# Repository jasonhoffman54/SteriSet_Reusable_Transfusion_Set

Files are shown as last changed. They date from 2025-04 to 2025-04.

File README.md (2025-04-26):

# Reusable Blood Transfusion Set – Handoff Documentation

This repository contains all files related to the development and handoff of a reusable blood transfusion set for the Pothawira Surgical Center in Malawi. The goal of this project is to provide a cost-effective, sterilizable, and sustainable solution to address critical blood transfusion needs in low-resource settings.  
It is intended as a resource and starting point for future teams at the Malawi University of Business and Applied Sciences (MUBAS) and other collaborators working to continue and improve the project.

---

## Repository Structure

### `STEP_Files`
- **Description:** Contains CAD files for the transfusion set design, organized into STEP files for different versions of the set.
- **Subfolders:**
  - `STEP Files`: Includes design iterations.
    - `V1 Transfusion Set`: Initial design components.
    - `V2 Transfusion Set (Working)`: Updated working designs.
    - `V3 Transfusion Set`: Latest version with improved locking mechanism and flow regulation.

### `Design`
- **Description:** Documentation related to the design process.
- **Subfolders:**
  - `Brainstorming`: Contains initial ideas, parts research, and material notes.
  - `Trade Studies`: Includes comparative analysis of design options.

### `BME462_Documentation`
- **Description:** General documentation for the project when in the bme 462 course.
- **Subfolders:**
  - `Meeting+Interview_Notes`: Notes and audio files from interviews and meetings.
  - `Oral_Presentations`: PowerPoint files for team presentations.
  - `Writing_Assignments`: Comprehensive written reports on project progress.

### `Handoff_Documentation`
- **Description:** Core documents intended for project continuation and future development at MUBAS.
- **Contents:**
  - `Handoff Outline`: Overview of project status, unresolved challenges, and recommendations.
  - `Bill of Materials`: Detailed list of components and materials used.
  - `Outsourcing Documentation`: Information to support sourcing and manufacturing.

### `Regulatory_Standards`
- **Description:** Regulatory and compliance documentation for the transfusion set.
- **Subfolders:**
  - `Data_Sheets`: Specifications and material details, including the Infinity Bond adhesive datasheet.
  - `ISO_Documents`: Relevant ISO standards for compliance.
  - `Malawi Regulations`: Overview of Malawian regulatory requirements for medical devices.

### `Testing`
- **Description:** Testing protocols and results for evaluating the performance and reliability of the design.
- **Subfolders:**
  - `Testing_Protocols`: Procedures and metrics for verification and validation.
  - `Testing_Results`: Results and analysis from executed tests.

### `Presentation_Material`
- **Description:** All final presentation materials used during the project timeline.
- **Contents:**
  - Presentation posters, slides, and supporting visuals from design reviews and final presentations.

---

## Contributions
This project has been made possible by the efforts of:

- **Team Members:**
  - Jason Hoffman
  - Hannah Kragt
  - Darcy Ayers
  - Michaela Harris

- **Advisors and Contributors:**
  - Dr. Anne Alaniz, DO
  - Dr. Joanie Hope, MD
  - Dr. Nancy Kragt, DO
  - Dr. Megan Madonna, Ph.D.
  - Matt Brown
  - Kerry Eller
  - Duke Pratt School of Engineering

---

## Project Handoff Note
This repository is designed to support the continuation and future development of the reusable blood transfusion set project. We encourage future teams to build upon these materials, continue design refinement, pursue regulatory alignment, and adapt the device to meet the evolving needs of healthcare providers and patients in Malawi.

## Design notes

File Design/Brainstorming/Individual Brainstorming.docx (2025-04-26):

Individual Brainstorming

Darcy

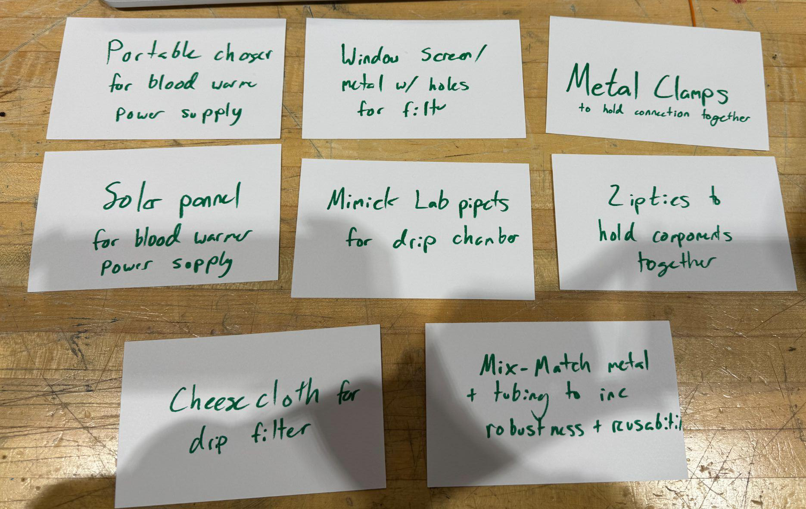
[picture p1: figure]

- Portable charger
  - Considers the power outages in Malawi
  - Meets the design criteria of using low-power
  - Meets the design criteria of being compact
  - Does not meet the design criteria of resource availability in Malawi
- Window screen/metal mesh
  - Meets the design criteria of sterilizable, reusability, and mechanical robustness
  - Depending on the material, this idea could fail in terms of resource availability and cost
- Metal connections
  - Meets the design criteria for sterilizable, reusability, mechanical robustness
  - This could not provide an air-tight seal, depending on whether there is no additional connections, such as glue
- Solar panel
  - Again, this accounts for power outages in Malawi
  - Meets design criteria for using low power and resource availability
  - Fails the design criteria of being compact
- Lab pipette for drip chamber
  - This material would allow for the flexibility we want in the chamber
  - This idea meets none of our major design criteria
- Zip ties for flow regulation
  - This allows for proper flow modulation
  - Meets the design criteria for sterilizable, reusability, cost, and ease of use
  - Fails the design criteria for resource availability and mechanical robustness
- Cheesecloth for filter
  - This would provide the design to filter out blood clots, however, the holes may be too large to efficiently filter.
  - Meets the design criteria for resource availability and cost
  - Fails the design criteria for sterilizable, reusability, and mechanical robustness
- Metal tubing in some locations
  - This idea was mainly to think of ways to make our tubing more robust
  - Meets the design criteria for sterilizable, reusability, mechanical robustness, and cost
  - Might fail the design criteria for air-tight seal due to additional connections

Hannah

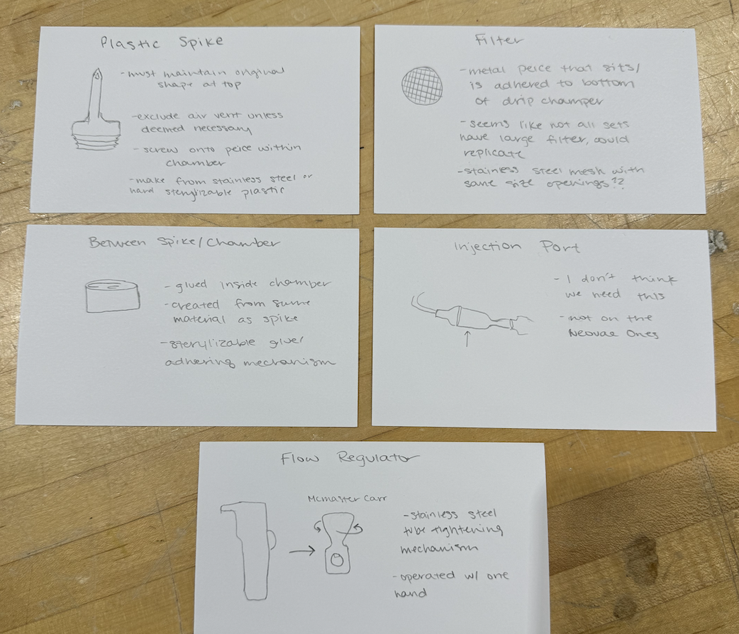
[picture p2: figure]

Jason

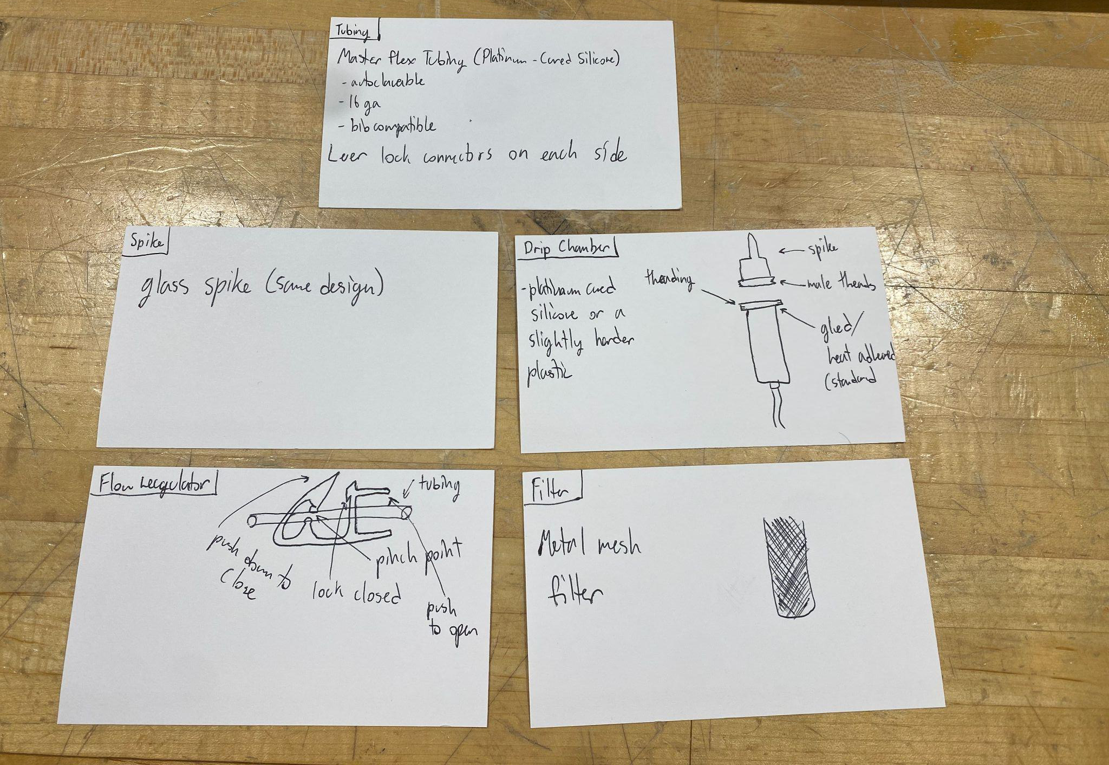
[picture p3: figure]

- Masterflex Tubing:
  - I found this steralizable tubing through research and it seemed perfect for our project
  - Meets design criteria of being autoclaveable, and biocompatible
  - The only part not considered is if the luer locks will hinder the sterilization process
- A Glass spike was thought to be a spike made of an easily sterilizable material.
  - Meets the design criteria of sterilizable and would be compatible with the blood bags
  - Does not consider the damage that could be done to the blood bag if too sharp
  - Does not consider durability and the likelihood that it will be broken in the clinic
- The Drip Chamber idea was thought to use the same material of the tubing that i found and make the spike attach to the drip chamber using a screw-on set with hard plastic or metal to make the chamber open and sterilizable.
  - Meets the design criteria of sterilizable and easy to assemble.
  - Does not consider what kind of adhesive we will use to attach the components
- The Flow regulator design was a design that I had seen online that i later found out was called a Robert Clip.
  - Meets the design criteria of being easy to use and sterilizable if made out of the right material.
  - Is not sufficient to provide a range of flow modulation in both increasing and decreasing flow
- The filter design was just a thought to make a metal mesh filter
  - This meets the design criteria of being a sterilizable material, however, does not consider whether the mesh size or porosity of the mesh will affect the sterility of the mesh
  - Would need to consider corrosion and other factors that would play into choosing the right metal
  - Also does not consider geometry for this filter which would have a large impact on the design.

Michaela

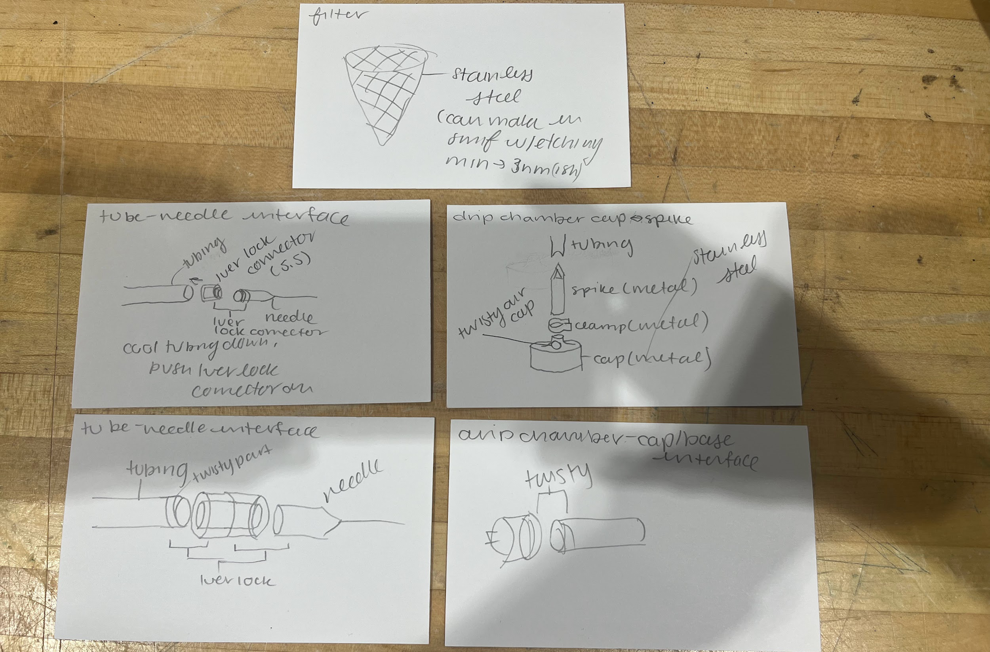
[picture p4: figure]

- Design 1 - Filter
  - Filter made out of metal mesh
  - Sterilizable, durable, reusable, easy to source
  - May be hard to assemble depending on how we put into drip chamber
  - Large surface area = faster blood filtration rate
- Design 2: Tube-needle interface
  - Tube- needle interface
  - Luer lock is airtight, easy to assemble, sterilizable, durable after many uses
  - Medical grade epoxy glue will ensure the strength of the connection from the tube to the luer lock
- Design 3: drip chamber cap/spike
  - Fit into each other
  - Lots of components makes it hard to assemble but improves sterilization capabilities
  - More components may mean less tight
  - Air vent not necessary if we have squishy bags
- Design 4: Tube-needle interface
  - Dual end luer lock connector with threads on tubing
  - Threads on tubing not feasible if have a bending material, would not be airtight and would be difficult to use
- Design 5: Drip chamber - cap/base interface
  - Have screw in for the cap and chamber
  - Airtight, easy to use, increases exposable surface area in autoclave
  - May have to use epoxies and additional components to finalize screw in

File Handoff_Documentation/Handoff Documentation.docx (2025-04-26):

# Project Overview

## Project Name & Description

Name: Reusable Blood-Giving Set for Pothiwira Surgical Center

The project focuses on developing an affordable, reusable, and sterilizable blood-giving set for the Pothawira Surgical Center in Salima, Malawi. Given the region’s high maternal mortality rate and limited access to blood transfusion supplies, the clinic faces critical shortages that delay life-saving procedures. The design integrates a durable twist-and-lock mechanism, a redesigned drip chamber for enhanced filtration, and a roller clamp for precise flow regulation. Materials such as platinum-cured silicone and stainless steel ensure biocompatibility and sterilization compliance. Testing confirmed the system’s ability to withstand compressive forces and effective bacterial removal after autoclaving. This solution aims to provide a sustainable alternative to single-use transfusion sets, improving patient care and healthcare accessibility in the region.

## Objective & Goals

Our primary goals for our project are:

1. Our design must be safe and sterilizable by passing tests that include bacterial removal, blood adhesion, and biocompatibility.
2. Make our design be durable, withstanding certain compressive strength and a drop test.
3. Ensure that our design is functional, including being easy to use, having no leakage, having flow modulation, having filtration, and is a compact size similar to standard disposable blood-giving sets.
4. Our design must fit community design requirements, including community comfort, use locally sourced materials, and low cost.

## Bill of Materials

Bill of Materials (https://docs.google.com/spreadsheets/d/1cqrfP7p347UXdv-eoOeXX8uZQHe5CB9nxKuMcwCITTk/edit?usp=sharing)

# Testing Procedures & Results

- Since we have all our testing from last semester already included in the git, maybe just add this new test to that document and link here?

# Assemebly & User Guides

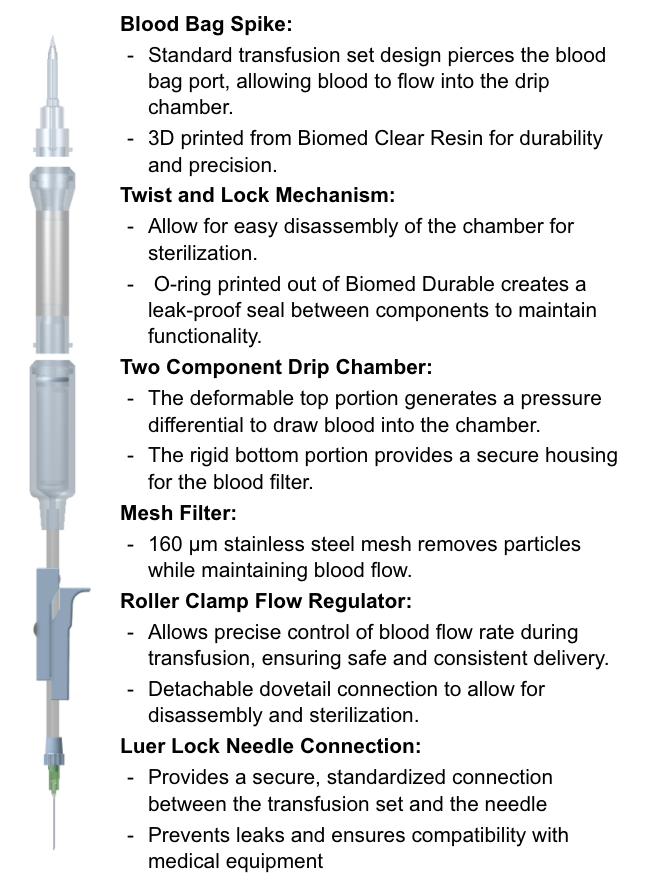
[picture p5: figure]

## Assembly of Set

1. Obtain the components listed above
2. Place the filter inside the rigid drip chamber
3. Twist and lock the flexible drip chamber to the rigid drip chamber
4. Attach the flow regulator to the tubing from the rigid drip chamber
5. Twist and lock the other side of the drip chamber of the spike
6. Attach the needle connection to the bottom of the tubing from the rigid drip chamber

## Disassembly & Sterilization of Set

1. Throw away the needle
2. Deconstruct the transfusion set by untwisting the spike from the flexible drip chamber and the rigid drip chamber.
3. Remove the filter cage from the rigid drip chamber
4. Place the 5 separate components (spike, flexible drip chamber, rigid drip chamber, and flow regulator) into the wash prior to autoclaving
5. Transfer the components into the autoclave and start a cycle of sterilization for 30 minutes at 121 ° C
6. After the cycle completion, remove the components

# Next Steps & Recommendations

### Unresolved Challenges

Adhesive Selection:
Finding a fully compliant adhesive remains an unresolved challenge. Both DOWSIL 734 and Infinity Bond adhesives failed to meet durability, biocompatibility, or sterilization requirements. Future work must identify a medical-grade, ISO 10993-certified adhesive capable of withstanding repeated autoclave cycles.

O-Ring Sizing and Performance:
The current O-ring design requires excessive compression at full engagement and does not provide a consistent seal across the locking range. Redesigning the O-ring geometry and groove depth is essential to create a reliable seal without placing unrealistic demands on assembly force.

Tolerancing of Components:
Variability in printed part dimensions has resulted in inconsistent assembly, poor sealing, and occasional mechanical failures. Further refinement of CAD models and manufacturing processes is necessary to achieve tighter dimensional control and consistent fit across all components.

Blood Adhesion and Surface Geometry:
Testing revealed residual blood in complex geometries and in sections with adhesive, posing a risk for incomplete sterilization. Smoother surface transitions, larger radii, and minimized internal crevices in addition to a medical grade adhesive are needed to improve sterilization outcomes and minimize infection risks.

### Design Change Recommendations

### Source a Medical-Grade Adhesive: The team should prioritize identifying a biocompatible, autoclavable adhesive, such as a medical-grade two-part silicone or epoxy. Early validation testing is critical to ensure that the new adhesive maintains strength and integrity through sterilization cycles.

Revise O-Ring Design:
Future prototypes should incorporate thicker O-rings and deeper seating grooves to allow gradual compression and better sealing. Expanding the compression zone can help accommodate small tolerancing inconsistencies without sacrificing seal integrity.

Introduce Modular Tubing Replacement:

Consider a design where the tubing is detachable and disposable after each use, while the hard components remain reusable. Quick-connect fittings could make the device safer, easier to sterilize, and better aligned with clinical workflows.

Improve Surface Geometry:
Components should be redesigned with polished surfaces, rounded internal geometries, and minimized seams to reduce blood adhesion. Post-processing of 3D-printed parts could further enhance sterilization efficacy.

Expand Mechanical and Functional Testing:
Subsequent prototypes should undergo full mechanical validation, including tensile, fatigue, and high-pressure leakage testing. Aligning testing protocols with ISO 1135-4:2015 standards will help prepare the device for future clinical approval and deployment.

## Key Partners and Contacts for Follow-up

Student Team Contacts

Hannah Kragt - hannah.kragt11@gmail.com

Jason Hoffman - hoffman.jason21@gmail.com

Darcy Ayers - darcy.ayers@gmail.com

Michaela Harris - mharris3002@gmail.com

Advisor Contacts

Megan Madonna - megan.madonna@duke.edu

Partner Contact

Anne Alaniz - abalaniz@houstonmethodist.org

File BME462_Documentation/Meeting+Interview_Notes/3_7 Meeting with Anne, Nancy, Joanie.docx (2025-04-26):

Meeting Outline

- Let them know we didn’t get Rice360
- Update on where we are with the project
  - Show them new printed parts (twist and lock, two part modulator, etc.)
  - Complications
    - Resin choice
      - Moving to either biomed durable or clear
    - Adhesive:
      - Darc update
        - Meets biocompatibility standards
        - Compatible with most sterilization techniques (good for 1st q)
      - Do they know of permanent, sterilizable adhesives?
    - Orings
      - Need platinum cured medical grade
      - Only ones we found quotes 60+ per
  - Future plans
    - Micheala testing
    - Handoff documentation
    - IP to hand off to MUBAS
      - Plan to hand off in spring
- Questions
  - If this is meant to one day be used at more than just Pothawira, should we be aiming to have a product that can be sterilized by a different technique
    - Have pots that they boil?
    - Chemical sterilization (spirit)
    - Most hospitals have autoclave
    - Will you have any other techniques at Pothawira Surgical? (Ex. Ethylene oxide ETO, Gamma irradiation, chemical disinfection)
  - Have any of you guys had experience with the regulation and approval of medical devices in Malawi / medical regulations in general with Pothawira?
    - Aida (public health) (Maggies sister) - connect that knows more about regulation and process
    - Ask Andrew (MUBAS)
- Questions from Anne, Nancy, and Joanie
  - Test to see if all sterilization techs are =, and device maintains structure
  - Is there a # of uses for the sets?

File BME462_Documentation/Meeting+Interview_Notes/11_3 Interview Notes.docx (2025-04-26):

Preplanning

- Go over the current solution
  - Ask about the need for an air vent
  - Ask about what type of needles they have or see if they could send us what brand of needles they have
  - Show the filter cage and say how there is a metal mesh
- How do we plan to change the current solution
  - Increase the diameter of the chamber
  - Twist and lock with silicone bumper for air tightness
- Go over the testing plan
  - Ask for advice on doing the community comfortability survey

Meeting Notes with Joanie and Anne 11/3/2024

Design

- shared design with stl files
- asked material - biomed resin, biocompatible, autoclavable
- confused about filter part - explained
- We dont have air vent - do you guys use it
  - Guess - get rid of air bubbles
  - ask lab guy they will be working with in salima what the air vent is for
  - asked nurse - too modern based on how they do it \
  - Maggie and matthew would know better - so will lab guys
    - she will send message to him
  - Put pictures of what we have right now in the group, she will send message to lab guys
- Talked about threaded components and issues we are worried about in the future pertaining to thread wear over time
  - liked the idea of making a slot connection and wanted to see what that would look like
  - Plan to do that in next prototype
- they asked if we have a way to modulate the flow
  - we have flow regulator, ok with design being the same
- asked about connection to needle, what does it look like there?
  - needles available
  - asked for pictures from them
- they asked if theres any part of system thats disposable
  - needle
- they asked how long is the tubing
  - 3-4 feet
  - based on standard sizing

Testing

- explained testing plan
- going to forward the testing metrics to them
- could ask them, translate, load them onto google doc
- on the ground they can print out survey, have patients answer questions when tyey come through the clinic
  - have a high volume clinic
- transfer, fill in on paper, put it back into google form for answering
- surveys
  - community members
    - comfort, don’t want to intimidate them
  - nurses
    - ease of use
  - one prior to any sort of use - ease of use, how does it feel, what does it look like
  - actual use = be different and more rigorous
  - Feedback from nurses for actual use
  - Patients be minimally frightened by the device
  - nurse - before using it and after using it survey
- Just got wifi and computers to facility - fast for staff (also english speaking) → make survey taking easier

Notes to update things from them

- Have 2 surveys for nurse
  - before use (autoclaving, ease of use)
  - using for patients
- is blood tested before it touches our set → yes
  - get packed RBCs
  - giving blood, do basic testing
    - HIV, HEPB, HEPC, hemoglobin

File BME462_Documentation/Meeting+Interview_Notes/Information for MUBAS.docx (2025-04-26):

Reusable Blood Transfusion Sets

Collaboration with Pothawira

Pothawira (Safe Haven) Christian Mission Organisation, based in Salima, Malawi, serves the community by providing housing, healthcare, education, and economic sustainability projects. The campus includes a medical clinic, birthing center, primary school, and a home for 124 orphaned children. Recently, funds were raised, and plans were made to open a new surgical center in 2025. This is crucial as the only other surgical center in the region, Salima District Hospital, has just two OR rooms, neither adequately equipped for optimal surgical procedures and insufficient to serve the needs of 800,000 people.

Blood Donation

Pothawira’s new surgical center will be equipped with a blood bank. Blood donation is a critical issue in Malawi, as the Salima District Hospital blood bank frequently lacks sufficient supply. Patients are required to bring a family member with the same blood type to be on standby for potential transfusions. This challenge is exacerbated when blood-giving sets are unavailable, as the Malawi Government provides a limited supply of these sets to the local hospital, but more are needed to reach the demand. This unfortunately leads to situations where necessary blood cannot be provided during surgery.

Needs Statement

The current method for blood transfusions at the Pothawira Surgical Center in Salima, Malawi, relies on on-site blood gathering, testing, and donation from a patient’s family member with the same blood type. The clinic lacks the ability to store blood donations and frequently runs out of necessary equipment for blood transfusions, leading to critical delays in patient care. The local population, which includes over 800,000 residents, is in urgent need of reliable and efficient transfusion methods. There is a need for affordable, reusable, and sterilizable blood-giving sets and a blood-warming device that can safely warm stored blood to the optimal transfusion temperature. These devices must be durable, compatible with existing equipment, and made from locally available materials to ensure sustainability, improving patient outcomes, and meeting the operational demands of the new blood bank and surgical center opening in 2025.

# Part 3:

Design criteria

1. Sterilizable (Must Have)

Justification: The blood-giving sets must be made with components that can withstand sterilization procedures used at the clinic (e.g., high-temperature cleaning). The blood-warming device must also be sterilizable to maintain safety in blood handling and administration.

Verification: We will test the device's components by subjecting them to multiple cycles of sterilization (e.g., autoclaving at 121°C for 30 minutes) and evaluating their structural integrity, material degradation, and cleanliness. Each component will undergo at least 50 sterilization cycles to verify long-term usability without degradation (21).

2. Locally available resources

Justification: The device should be made from materials that are available or easily accessible in Malawi to ensure long-term sustainability and reproducibility. This will reduce dependency on external suppliers and allow local healthcare providers to maintain and replicate the device.

Verification: A conversation will be conducted with local suppliers and healthcare providers in Malawi to confirm the availability of materials needed to manufacture the devices.

3. Cost under $100 for blood-giving sets

Justification: The cost of the devices must meet the budgetary constraints of the clinic and the Malawian healthcare system. These numbers are safe upper limits for cost, given by our sponsor. The affordability will ensure that the devices can be widely used and sustained in the resource-limited setting.

Verification: A cost analysis will be conducted by sourcing material quotes from local and international suppliers, along with labor costs. We will ensure the final production cost remains within the specified range.

4. Air-tight seal Justification: The blood-giving sets must maintain an air-tight seal to prevent contamination and ensure the safe transfer of blood. This is essential to avoid infection risks and maintain the integrity of blood during transfusion.

Verification: We will test the air-tightness by applying water or air pressure to the system and ensuring no leaks occur under typical use conditions. The system will also be tested under vacuum conditions to simulate blood flow during transfusion.

5. Reusable, Durability to withstand 200 uses Justification: The blood-giving sets must be reusable and durable enough to withstand multiple sterilization cycles and uses without degrading. This will ensure that the investment in each set maximizes its long-term use and reduces the need for frequent replacements.

Verification: The devices will undergo mechanical fatigue testing by simulating repeated use, including sterilization cycles, disassembly, and reassembly.

6. Portability and easy-to-use design Justification: The device should be portable and easy to use by healthcare workers with minimal training. This will facilitate use in various settings within the clinic and ensure the device can be employed efficiently during emergency situations.

Verification: The device’s portability will be verified by ensuring it weighs less than 2 kg and can be easily transported by a single healthcare worker between rooms. Ease of use will be validated through usability tests where healthcare workers will be able to set up the device within 10 minutes and operate it effectively after no more than 30 minutes of training.

7. Mechanical robustness and resistance to mechanical stress Justification: The devices must be able to withstand rough handling, transport, and drops in a busy clinic environment without breaking or malfunctioning. According to WHO standards, medical devices in resource-limited settings must be rugged and able to withstand rough handling, transport, and frequent use. This ensures longevity and reduces the cost of repairs or replacements.

Verification: The devices will be subjected to mechanical stress tests, including drop tests from 1 meter and impact resistance tests. Components will also be tested for fatigue by applying repeated pressure and strain.

8. Compact design for storage

Justification: The blood storage device must be of comparable shape and size to existing blood bags to fit seamlessly into the current blood storage infrastructure at the clinic. This ensures compatibility with existing refrigeration and storage systems, reducing the need for modifications or additional storage solutions.

Verification: We will compare the dimensions of the blood storage device to standard blood bags (approximately 10-15 cm in width and 20-25 cm in length) and test its fit in clinical storage units. The device must occupy the same space as a typical blood bag in refrigerators and storage racks used at the clinic, ensuring it integrates smoothly with the current setup.

9. Community Comfortability

Justification: The blood-giving set must be as non-intimidating as the current disposable sets to ensure patient comfort and acceptance, supporting a smooth transition and consistent use.

Verification: Surveys will compare patient comfort levels using a Likert scale, assessing the new set against existing disposable sets. Usability tests will gauge willingness and preference through direct comparison feedback.

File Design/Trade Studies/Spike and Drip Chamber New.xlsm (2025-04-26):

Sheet: Start Here
Trade Study Template for MS Excel
Version 2.0
Copyright © 2014 by Jeffrey Ellis. All rights reserved.
http://jeffreyellis.org
*** START HERE *** The Trade Study Template for MS Excel is a spreadsheet that implements a simple weighted sum method for multiple criteria decision making. It is a .xlsm file that should work with Excel 2007 and later. Instructions: 1. Read the license agreement on the License worksheet. Your continued use of this template constitutes agreement with this license. 2. In the Raw Data worksheet, enter your alternatives under consideration and your evaluation criteria, and enter the raw scores for evaluation criteria for each alternative. 3. In the Utility Functions worksheet, enter the data required to define the utility functions that transform raw scores into utility (on a scale of 0.0 to 1.0) for each evaluation criteria. 4. In the Evaluation worksheet, set and adjust the weighting factors for your evaluation criteria. This worksheet also displays a stacked bar chart of the results, with the alternatives sorted in ranked order. 5. In the Sensitivity Analysis worksheet, you can perform sensitivity analysis on any selected criteria.
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

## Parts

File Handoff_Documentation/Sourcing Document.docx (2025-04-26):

Platinum Cured Silicone O-rings

Fluid Path Products (https://www.fluidpathproducts.com/_files/ugd/faea02_0909baf2fb4c4fbfb870d9c755825b22.pdf)

- Have clear, platinum cured silicone O-rings in stock
- Need to know size, and quantity
  - If size the have already in stock, could receive relatively quickly
- Email: carlyb@fluidpathproducts.com
- ISO 10993 Compliant

Biocompatible Permanent Adhesive

- Needs to meet ISO 13485 an ISO 10993

Elastosil E43 N

- What we tried to originally purchase last semester
- Having a hard time finding a good sourcing location
- SkyGeek (https://skygeek.com/wacker-chemie-elastosil-e43-rtv-1-silicone-rubber-adhesive-90-ml-tube.html?gad_source=1&gbraid=0AAAAAD_KchHeS3hvwVfQXH2fucgE1NsRO)

Vitralit 4731 (https://www.panacol.com/panacol/datasheets/vitralit/vitralit-4731-english-tds-panacol-adhesive.pdf) & Vitralit 7041 F (https://www.panacol.com/panacol/datasheets/vitralit/vitralit-7041f-english-tds-panacol-adhesive.pdf)

- Need to be cured by UV/Visible Light
  - Confused if this means we need LED or not

Master Bond (https://www.masterbond.com/products/silicones-medical-devices)

- Mastersil 151 Med

GlueGun (https://www.infinitybond.com/products/infinity-bond-medical-device-cyanoacrylate-super-glue?variant=31582833901702)

# Infinity Bond Medical Device Super Glue Cyanoacrylate

  - 220 $
  - Requested TDS and SDS to confirm if usable
- Got TDS and SDS, emailed to try and get a sampe - if no response today will call tomorrow

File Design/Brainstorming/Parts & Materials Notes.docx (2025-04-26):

Blood Giving Sets

PVC: Gamma and sterilization stability, Migration resistance, Color consistency, Thermal stability, RF and solvent welding, Printability (link (https://www.eastman.com/Markets/Medical-Supplies/Pages/Medical-Tubing-Bags.aspx))

1. Bag
  a. Saline: Polypropylene (PP) - Sterilized by water cascade terminal sterilizer in house; eliminating the need for 3rd party sterilization services (link (https://isikel.com/manufacturing/saline-bags/))
  b. PVC
    i. 42 day shelf life
  c. Needs to have a port for donation and a port for transfusion (most had 3 ports tho?)
  d. If reusable must be resealable after donation/transfusion
  e. Needs anticoagulants (and for them to be replenished with each use
2. Protector
  a. Polyethylene (PE) - sterilizable
3. Plastic Spike
  a. Acrylonitrile butadiene styrene (ABS) - ABS can be sterilized, but not with an autoclave or gamma sterilization
4. Air Vent
  a. Stainless steel, ABS, or POM (polyacetal). The spike is encased in polyamide
  b. Air vent (https://www.kmedhealth.com/difference-between-vented-and-non-vented-iv-sets/) isn’t absolutely necessary unless transferring from rigid container
5. Drip Chamber
  a. DEHP PVC or Non-DEHP PVC - potentially toxic?
  b. Polyethylene terephthalate (PET or PETE) - sterilizable and flexible
  c. Drip Chamber + Spike (https://www.kmedhealth.com/product/drip-chamber-with-spike-48mm-and-50mm/)
  d. Needs to be able to be compressed
6. Filter
  a. Polypropylene (PP)
  b. Basic mesh filter with pore size of 170-260 microns
  c. https://sharevfilters.en.made-in-china.com/product/KmNrbVyYgnRP/China-Blood-Filter-for-Transfusion-Set.html
  d. Metal mesh with 125-micron filter link (https://www.amazon.com/Stainless-Steel-Filter-Screen-Filtration/dp/B07QNTQ13L?hvadid=693071814667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)
  e. Watchman device for LAA - PET fabric material link (https://www.watchman.com/en-us-hcp/about-the-procedure.html)
7. Tubing
  a. PVC and sometimes DEHP to add flexibility
8. Flow regulator
  a. PE or ABS
  b. Potentially could make from metal/order metal component
    i. https://www.mcmaster.com/5330K16/
    ii. https://www.mcmaster.com/products/pinch-valves/
9. Injection site
  a. Latex or Latex free
  b. Rubber Bulb Injection Site (https://www.kmedhealth.com/product/rubber-bulb/)
10. Luer Lock Connector
  a. ABS
  b. Pre-made order?
  c. Will need connectors for each component not necessarily this type but airtight and reusable
11. Needle
  a. Non sterilizable/ reusable
12. Other material links
  a. https://www.kmedhealth.com/types-of-iv-set-injection-sites/

Wednesday

- Understanding of how each component works

First prototype

1. Blood bag - Ziploc bag
2. Plastic spike -
3. Drip chamber - squeeze bottles
4. Filter - cheese cloth
5. Tubing - tubing or plastic straws
6. Injection site
7. Luer lock - plastic syringe luer lock
8. Needle - sewing needle

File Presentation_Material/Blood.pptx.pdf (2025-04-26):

# Reusable Blood Giving Sets for Pothawira Surgical Center

## Hannah Kragt, Jason Hoffman, Micheala Harris, and Darcy Ayers - Fall 2024

## Design Project Goal

Our project aims to create an affordable, reusable, and sterilizable method for blood-giving sets to address the limited availability of single-use sets for the Pothawira Surgical Center in Salima, Malawi.

## Background and Motivation

- High Maternal Mortality Rates:
– 25th highest maternal mortality rate in the world¹
– Blood loss due to postpartum hemorrhaging (PPH) is the leading cause of maternal mortality³
- Challenges in Blood Supply:
– Salima, Malawi, serves a population of 560,000 but only receives 10 units of blood per week from the government⁴ – Blood has a very short shelf life, often lasting less than 4 hours without proper storage⁵
– Blood is only donated when a relative is in urgent need⁴
- Inadequate Healthcare Facilities:
– Patients commute 2 hours away to get transfusion sets⁴ – Many women give birth on the floor of clinics without adequate care or clean environments⁴
- Current solutions are not sustainable
– Disposable solutions are not easy to source or store⁴

## Final Design Solution

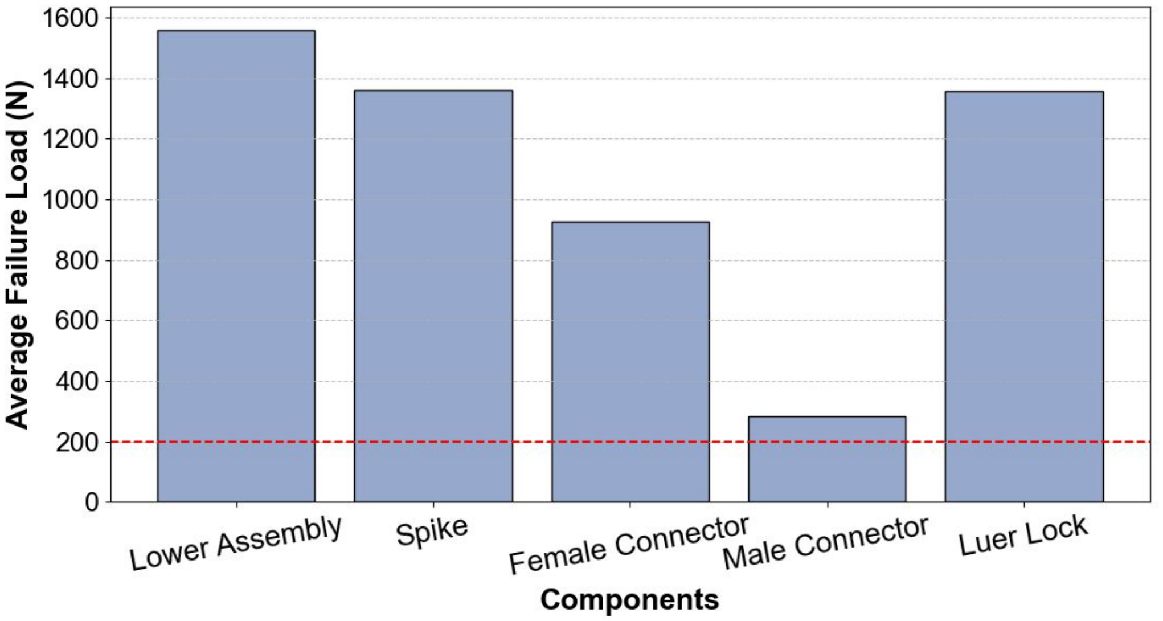
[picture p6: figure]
Temperature: 37.0°C

We would like to extend our thanks to the following:
- Dr. Anne Alaniz DO
- Dr. Joanie Hope MD
- Dr. Megan Madonna Ph.D.
- Matt Brown
- Kerry Eller
- Duke Pratt School of Engineering

## Acknowledgements

## Results

## Conclusions and Future Work

- Twist-and-Lock Mechanism: Replaced screw-in components with a twist-and-lock system for durability, airtight sealing, and ease of use, using a platinum-cured O-ring
- Redesigned Drip Chamber: Larger chamber for robust, industry-standard filtration
- Enhanced Flow Modulator: Improved modulation control, ridged roller, stronger walls, removable design
- Sealant Replacement: Identify a biocompatible alternative to DOWSIL 734 to ensure compliance with ISO 10993 standards

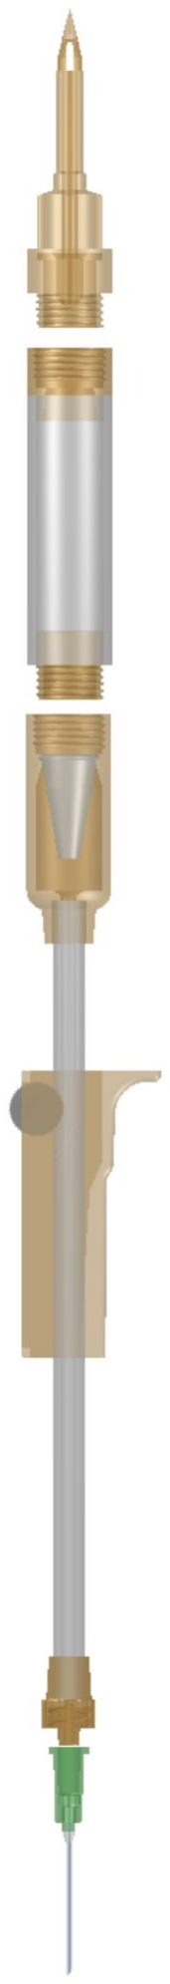
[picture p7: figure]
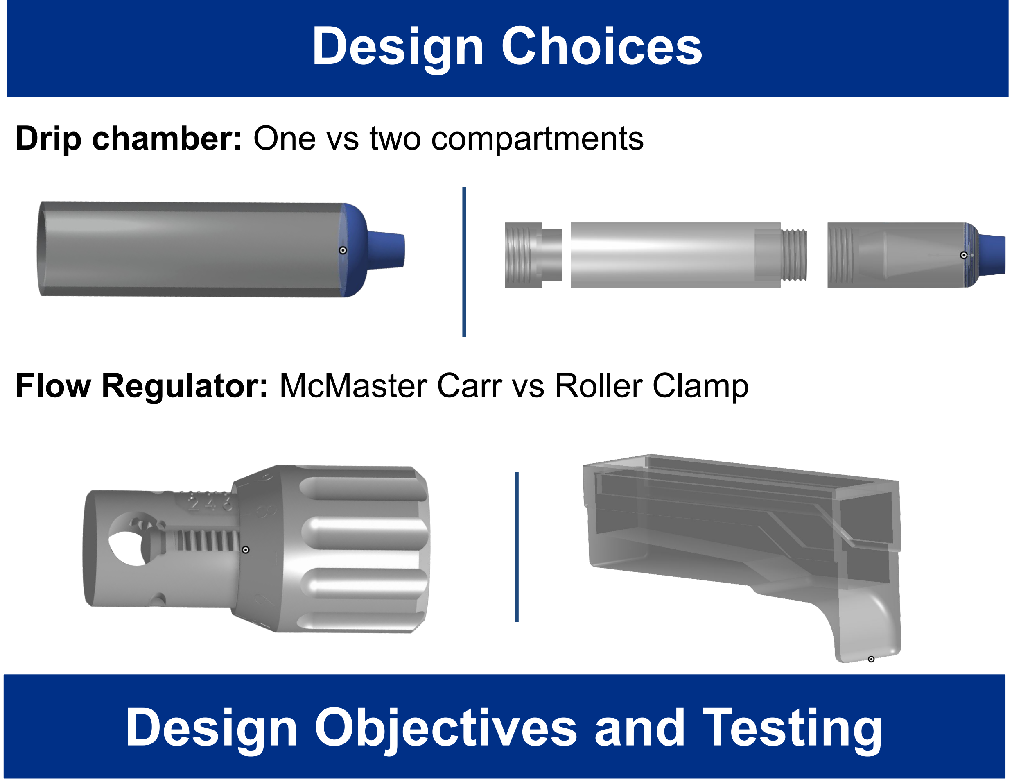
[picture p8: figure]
Design Objectives and Testing; Design Choices; Drip chamber: One vs two compartments

Design Objective | Test | Results
Ensure effective bacterial removal from the set after sterilization | Autoclaved components (clamp, mesh, tubing) at 121°C for 40 min; 10 analyzed bacterial growth (E. coli) using ImageJ | PASS - No bacterial growth observed
Transfusion set is leak-proof during use | Assembled set with Ziploc bags filled with water; simulated use and observed for leakage at connections | PASS - No significant leakage in 5 tests; minor leakage in 1 test due to puncture seal
Verify that all materials in the set are biocompatible and met ISO 10993 standards | Reviewed material data sheets and product descriptions for compliance with biocompatibility standards¹¹ | FAIL - Majority of materials passed; Dowsil 734 Sealant failed, requiring replacement
Components can withstand a minimum lateral compressive load of 200 N | Applied lateral force using a vice and measured load at failure with a high-capacity scale | PASS - All components passed
Cost-efficient for affordability in resource-limited settings | Conducted cost analysis using BOM; calculated per-set cost based on material quotes | PASS - Total cost was $23.71 per set

Resin
(Roller
clamp)

Metal Mesh
(Filter)

Platinum-Cured
Silicone Tube

(-) Control
(glass
beaker)

(+) Control
(colonies in
tube)
Material | Use | Attributes
Biomed Amber Resin | 3D Printed Components | Biocompatible, rigid, 6 semi-transparent
Platinum-Cured Silicone | Tubing | Flexible, biocompatible, 7 sterilizable
304 Stainless-Steel Mesh | Filter | Corrosion-resistant, durable, 8 efficient
DOWSIL Flowable Sealant | Permanent Adhesive | Airtight, easy application, 9 food grade

## References

[1] CIA., “Maternal mortality ratio”, 2024
[2] Kalulu et al., “Determinants of teenage pregnancy in Malawi” BMC Women’s Health, 2024
[3] Beltman et al., “Beyond maternal mortality” Acta Obstet Gynecol Scand, 2011
[4] A. Alaniz and J. Mayer Hope, “The Blood Transfusion Set Deficiency In Salima, Malawi,” 2024.
[5] Brunskill et al., “What Is the Maximum Time That RBCs Can Be Left Out?,” Transfusion Med. Reviews, 2012
[6] Formlabs et al., BioMed Amber Resin Tech. Data Sheet, 2023.
[7] Avantor Fluid Handling et al., Cert. Qual. Tubing MFLEX Silicone No. 16, 2024.
[8] Xu et al., J. Mater. Res. Technol., 2024.
[9] Dow Chemical Company et al., DOWSIL 734 Flowable Sealant Tech. Data Sheet, 2020.
[10] CDC et al., Steam Sterilization 2024
[11] FDA et al., Use of ISO 10993-1 Guidance, 2023.
E. coli Removal Results: Device is able to be sterilized without bacterial growth after autoclaving

Blood Bag Spike:
- Standard transfusion set design pierces the blood bag port, allowing blood to flow into the drip chamber.
- 3D printed from Biomed Amber Resin for durability and precision.
Threaded Connections:
- Allow for easy disassembly of the chamber for sterilization.
- Create a leak-proof seal between components to maintain functionality.
Two Component Drip Chamber:
- The deformable top portion generates a pressure differential to draw blood into the chamber.
- The rigid bottom portion provides a secure housing for the blood filter.
Mesh Filter:
- 160 µm stainless steel mesh removes particles while maintaining blood flow.
- Designed with a lip for secure placement in the drip chamber.
Roller Clamp Flow Regulator:
- Allows precise control of blood flow rate during transfusion, ensuring safe and consistent delivery. Luer Lock Needle Connection:
- Provides a secure, standardized connection between the transfusion set and the needle
- Prevents leaks and ensures compatibility with medical equipment

Flow Regulator: McMaster Carr vs Roller Clamp

Compressive Failure Test Results: All components of device can withstand compressive force of 200N

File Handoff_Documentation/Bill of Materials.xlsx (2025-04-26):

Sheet: Sheet1
Material/Component | Link | Cost per unit | Data s

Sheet: Sheet2
Material/Component | Destributer | Link | Cost per unit | Data Sheet (if available) | Comments
Masterflex® L/S® Precision Pump Tubing, Platinum-Cured Silicone, L/S 16; 25 ft | MasterFlex | https://www.avantorsciences.com/us/en/product/NA5144597/masterflex-l-s-precision-pump-tubing-platinum-cured-silicone-avantor | $110 / 25 ft | 39649788.pdf (https://drive.google.com/file/d/1tNDcIT6IlDR5QIraNRWExZWtzMHCHnJR/view?usp=sharing) | Platinum-Coated Silicone Tubing (I.D: 3mm)
Cold & Colder Ultra Clear Pure Silicone Tubing by the foot | Cold & Colder | https://coldandcolder.com/collections/featured-products/products/silicone?variant=41786948157613 | $1.95 / ft | Cold & Colder Tubing (https://docs.google.com/document/d/1e-jHgzZKUy4-TXI4_C50p3UIj-2hbJyQbGJ7OiWKfCQ/edit?usp=sharing) | Platinum-Coated Silicone Tubing (I.D: 25.4mm)
Dowsil 734 Flowable Sealant | Dowsil | https://www.aerospheres.com/products/sealants/elastosil-e43-90-ml-tube/ | $52.40 | 95-1058-01-dowsil-734-flowable-sealant.pdf (https://drive.google.com/file/d/1FSC-Weza_c-cbWSuwQx6nmtAhDPpoqPI/view?usp=sharing) | Original Adhesive, Doesn't meet ISO 10993 Standard
Biomed Clear Resin | Formlabs | https://formlabs.com/store/materials/biomed-clear-resin/?_bt=715361922394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 | $349/L | 2001432-TDS-ENUS-0.pdf (https://drive.google.com/file/d/1d4uA7wYFVtt3jQ1FuF137jnkkdj8VKLk/view?usp=sharing) | For printing all rigid components, use roughly 60ml per print
Biomed Elastic Resin | Formlabs | https://formlabs.com/store/materials/biomed-elastic-50a-resin/ | $349/L | 2302832-TDS-ENUS-0.pdf (https://drive.google.com/file/d/1flWeDUGft7DmXhl38e5WYCV_0fZufky9/view?usp=sharing) | For printing compressable O-rings
304 Stainless Steel Woven Wire 80 Mesh 0.18mm Hole | Amazon | https://www.amazon.com/304-Stainless-Steel-Woven-Wire/dp/B07ZQ1ZCKJ?hvcampaign=business&gbraid=0AAAAA-bxZAHeOU6dPf0GyaMTzGCgFVEsY | $3.72/sq ft | Steel Mesh (https://docs.google.com/document/d/1AruYmwrgTkx_dW1E24qpgE6N79BoQdFs-MYufgR2YGg/edit?usp=sharing) | For the mesh filter

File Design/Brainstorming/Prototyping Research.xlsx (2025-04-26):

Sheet: Sheet1
Description | Material Purchase Links | CPU ($)
Sterilizable Tubing | link (https://us.vwr.com/store/item/NA5144597/masterflex-l-s-precision-pump-tubing-platinum-cured-silicone-avantor) | 20
Blood Transfusion Set Components | link (https://www.kmedhealth.com/what-is-a-blood-transfusion-set/)
Medical Grade Plastics | link (https://www.kmedhealth.com/what-are-medical-grade-plastics/)
Bulk Order links - luer lock, rubber bulb, rubber pad | link (https://www.kmedhealth.com/types-of-iv-set-injection-sites/)
Sterilizable drip chamber with method of creation and parts list | Transfusion Drip Chambers | GVS (https://www.gvs.com/en/catalog/transfusion-drip-chambers)
Pinch Clamps/Screw Clamps to replace flow regulator | link, link (https://www.mcmaster.com/5330K16/)
Elastosil E43 (90ML Tube)
Filter - holes in metal | Etched Plates for Filtering and Anti-dust (https://www.perforated-sheet.com/perforatedsheetapplication/etched-palates.html) |  | Could potentially make this in SMIF
Tubing - silicone, cheap, larger diameter than desired | https://www.govets.com/usa-sealing-inc-310-28569309.html

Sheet: Sheet2
MATERIAL | use | PRO | CON |  | blood bag
Glass | - Spike - Cap/base of drip chamber | Autoclavable | Breaks easily |  | spike
Rubber | - Blood bag - Rubber bulb | Autoclavable |  |  | tubing
Silcone | - Tubing - Drip chamber | Autoclavable (250ºC), cheap |  | https://www.govets.com/usa-sealing-inc-310-28569309.html | cap of drip chamber
Stainless steel | - Clamp - Filter | Autoclavable |  | https://www.perforated-sheet.com/perforatedsheetapplication/etched-palates.html | clamp
 |  |  |  |  | filter
 |  |  |  |  | drip chamber
 |  |  |  |  | base of drip chamber
 |  |  |  |  | rubber bulb
 |  |  |  |  | hypodermic needle

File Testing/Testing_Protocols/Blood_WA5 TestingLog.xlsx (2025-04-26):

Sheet: Master Plan
Design Requirements |  | Method of Verification (BOM, X type of testing, self-evident by dimension X, etc). | If you know there would be a method to test that you want to do, but in discussing with the instructional team know it may not be feasible within the class framework, make a secondary plan for a simulated testing procedure that may work towards the goal within the limits of the class in addition to the "If we could, we would do this" plan. |  | Reporting | Target Completion Date | Required Materials/Prep | Comments
 |  |  | Ideal Testing Plan (Lay out plan for testing generally, as detailed as possible) | Preliminary Testing Plan (Lay out plan for testing generally, as detailed as possible)
1.1 | Safety/Sterilizability
 | Bacterial Removal | Sterilization Testing | Add 1 mL of bacteria to each component and metal surgical tube. Incubate for 48 hours. Then wipe down with kimwipe for 15 seconds. Place component in autoclave. Once done, remove from autoclave, look under microscope for bacteria. | Add 1 mL of bacteria to each component and metal surgical tube, then wipe down with kimwipe for 15 seconds. Place component in autoclave. Once done, remove from autoclave, look under microscope for bacteria. | Determine and record % of surface area covered by bacteria at 5 different locations for both surgical-grade metal and each component | 2024-11-08 | Equipment and instruments needed: Autoclave, Each component of our device, Surgical-grade metal, Light microscope, Bacteria stock of Escherichia coli Reusable glassware/plasticware needed: Eppendorf tubes (1.5mL) x12 Disposable materials needed: Pipettes (1000µL), Kimwipes
 | Blood Adhesion | Performance Testing | Fill beaker with 10 ml of animal blood. Place medical-grade metal in beaker, place component in beaker, mix by swirling around with hand for 1 minute to simulate blood running along surface of material. Then extract component and medical-grade metal and place component and medical-grade metal in autoclave. Remove from autoclave and take photo of component and medical-grade metal for later reference. | Mix 5 mL PBS and 5 mL of red food dye in large 2000mL beaker. Place medical-grade metal in beaker, place component in beaker, mix by swirling around with hand for 1 minute to simulate blood running along surface of material. Then extract component and medical-grade metal and place component and medical-grade metal in autoclave. Remove from autoclave and take photo of component and medical-grade metal for later reference. | Remove from autoclave and take photo of component and medical-grade metal for later reference. Observe if any red dye is visible, qualitatively compare to amount visible on metal | 2024-11-08 | Equipment and instruments needed Red food dye, Phosphate Buffered Saline (PBS), Motorized pipette filler, Transfusion set components Reusable glassware/plasticware needed Beaker Disposable materials needed Serological pipette,Vacuum pipette
 | Biocompatibility | Self-evident by BOM | Compile a comprehensive Bill of Materials (BOM) for the blood-giving sets. Review data sheets for each material used in the design to verify biocompatibility. Cross-check materials against biocompatibility standards. | Compile a comprehensive Bill of Materials (BOM) for the blood-giving sets. Review data sheets for each material used in the design to verify biocompatibility. Cross-check materials against biocompatibility standards. | Compile biocompatibility of all materials and summarize findings in testing document | 2024-11-08 | List of materials and corresponding BOM for each material
2.1 | Durability
 | Compressive Strength | Strength Testing | Prepare each component of the blood-giving set for testing by measuring its initial dimensions using calipers. Place the component into the compression testing machine. Apply a gradually increasing compressive force until the component breaks or malfunctions. Record the maximum load at failure for each component. Repeat the test for each individual component of the blood-giving set 3 times each. | Prepare each component of the blood-giving set for testing by measuring its initial dimensions using calipers. Place the component into the compression testing machine. Apply a gradually increasing compressive force until the component breaks or malfunctions. Record the maximum load at failure for each component. Repeat the test for each individual component of the blood-giving set. | Record the maximum load at failure for each component. Repeat the test for each individual component of the blood-giving set. | 2024-11-04 | Materials to be tested including: tubing and 3D printed components. Conduct testing in lab with compression testing machine, report findings.
 | Drop Strength | Drop testing | Separate each component from the blood giving set, drop each component onto concrete floor from a 1m height. Repeat 3 times per each component. Note any visible abrasions/damage to the material, take a picture of the material at each level of dropping. | Separate each component from the blood giving set, drop each component onto concrete floor from a 1m height. Repeat 3 times per each component. Note any visible abrasions/damage to the material, take a picture of the material after each round. After damaging piece, put back into set, run water through. If set does not leak after all trials, component passes test. | Record observations for each component for each time dropped and whether or not the material leaks after all the tests. | 2024-11-05 | Transfusion test, phone camera
3.1 | Functional Requirements
 | Ease of Use | User Survey | Create an assembly and sterilization guide and have 20 doctors and nurses set up the transfusion set and using a Qualtrics survey rate the ease of use of our design on a likert scale (strongly agree, agree, disagree, strongly disagree) to four questions regarding the instructions, assembly, flow modulation, and disassembly. We also have included a comments section for expansion on their rankings. | Create an assembly and sterilization guide and have 10 classmates set up the transfusion set and using a Qualtrics survey rate the ease of use of our design on a likert scale (strongly agree, agree, disagree, strongly disagree) to four questions regarding the instructions, assembly, flow modulation, and disassembly. We also have included a comments section for expansion on their rankings. | Collect user surveys rating the ease of use of our design on Likert scale (strongly agree, agree, disagree, strongly disagree) | 2024-11-11 | User-survey, timer, and set up instructions to perform the test. Ask 10 students to perform the setup and complete the survey.
 | Leakage | Leakage Testing | Set up the transfusion set. Puncture a bag filled with PBS and evaluate and points on leakage in the tubing and connections. Have a bin under the set to quantify unwanted leakage. Have a separate bin to collect PBS from needle tip. Repeat 10 times. | Set up the transfusion set. Puncture a bag filled with PBS and evaluate and points of leakage in the tubing and connections. Have a bin under the set to quantify unwanted leakage. Have a separate bin to collect PBS from needle tip. Repeat 5 times. | Collect PBS from bin under the transfusion set. Measure the water in the bin to quantify the amount of water that leaks out during the test. Average the scores from the trials. | 2024-11-04 | Ziploc with PBS, transfusion set, beakers to perform the test. Repeat test 5 times and record amount of water that leaked.
 | Flow Modulation | Flow Testing | Set up the transfusion set. Set the flow modulation at fully open, and let water flow through set for 2 minutes. Collect water from needle tip in a beaker. Weigh water in beaker and using math determine flow rate. Repeat this step in very small increments until fully closed. | Set up the transfusion set. Set the flow modulation at fully open, and let water flow through set for 2 minutes. Collect water from needle tip in a beaker. Weigh water in beaker and using math determine flow rate. Repeat these steps for 75%, 50%, and 25% flow modulation until fully closed. | Collect water from beaker. Determine flow rate at each modulation level using math. Create a report to analyze the modulation | 2024-11-04 | Transfusion set, beaker, water, scale, and math formulas. Alter flow modulation levels and record amount of water in end beaker.
 | Filter | Filtration Testing | Mix 250mL PBS with 40mg of 80µm glass beads in 500mL beaker. Hold filter and base above second beaker, pour mixture from first beaker through to second beaker, let it drip for 30 seconds. Hold industry-standard blood filter above third beaker, pour contents from second beaker through and let filter drip for 30 seconds into third beaker. Take contents of industry-standard filter, pour onto plastic holder, ensure that only beads are on scale Determine and record weight of beads filtered out by industry-standard filter that were not filtered out by the filter and base from transfusion set Repeat 5x | Mix 250mL PBS with 40mg of 300µm glass beads in 500mL beaker. Hold filter and base above second beaker, pour mixture from first beaker through to second beaker, let it drip for 30 seconds. Hold industry-standard blood filter above third beaker, pour contents from second beaker through and let filter drip for 30 seconds into third beaker. Take contents of industry-standard filter, pour onto plastic holder, ensure that only beads are on scale Determine and record weight of beads filtered out by industry-standard filter that were not filtered out by the filter and base from transfusion set Repeat 3x | Determine the weight filtered out by the second filter to determine if it is within our target | 2024-11-06 | Equipment and instruments needed Filter and base from blood transfusion set, Industry-standard blood filter and drip chamber, 80µm diameter glass beads. PBS bottle,Gram scale Reusable glassware/plasticware needed Beakers (500mL) Disposable materials needed Plastic holder
 | Compact Sizing | Self-evident by dimension of set | Determine the length, width, and height of device in final packaging to be stored on hospital shelfs. Confirm our dimensions are similar in size to current disposable blood giving set used | Determine the length, width, and height of device in a ziploc bag to be stored on hospital shelfs. Confirm our dimensions are similar in size to current disposable blood giving set used | Determine the length, width, and height of device when wrapped up for storage. | 2024-11-06 | Transfusion set Ziploc bag Calipers
4.1 | Community Design Requirements
 | Community Comfort | User Survey | Create Qualtrics survey with questions about various community comfort points surrounding our product and in partnership the surgical center, have them hand out a 4 question survey to 100 patients about their impressions of our device during implementation in the surgical center. | Create Qualtrics survey with questions about various community comfort points surrounding our product. Hand out a 4 question survey to 10 classmates about their impressions of our device. | Record responses and critically analyze the trends found in them from the Likert scale of 1 (Strongly disagree) to 5 (Strongly agree) | 2024-11-11 | Create survey with questions to gauge community comfort with our design
 | Local Sourcing | BOM & User Survey | Create a list of all materials we plan to use in our design and create a BOM to ensure the materials are locally sourced. Cross check our findings with our client and connections at Malawi Polytechnic | Create a list of all materials we plan to use in our design and survey our partners at Malawi Polytechnic on the local availability of them | Compile a list of our materials and create a document ranking their resource availability on a scale from 1-5 with 5 being the easily found in Malawi | 2024-11-08 | List of materials used in our design. Research whether those materials are available locally in malawi.
 | Cost Efficient | Self-evident by BOM | Determine the price of each component used in the transfusion set. Sum up the total cost of the set. | Determine the price of each component used in the transfusion set. Sum up the total cost of the set. | Report cost for each component and total costs of set | 2024-11-08 | List of materials used in our design. BOM of those materials with prices

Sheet: Schedule
Test | Design Requirements Being Tested | Things to test/report | Start Date | Target Completion Date | Target Reporting Completion
Bacterial Removal | Safe and Sterilizable | % of bacteria present | 2024-11-04 | 2024-11-06 | 2024-11-10
Blood Adhesion |  | Visibility of red food dye | 2024-11-04 | 2024-11-06 | 2024-11-10
Biocompatibility |  | Biocompatibility according to BOM | 2024-11-05 | 2024-11-05 | 2024-11-10
Compressive Strength | Durable | Maximum load at failure | 2024-11-04 | 2024-11-04 | 2024-11-06
Ease of Use | High Performance | User survey feedback | 2024-11-07 | 2024-11-11 | 2024-11-11
Leakage |  | Amount of leakage observed | 2024-11-04 | 2024-11-04 | 2024-11-06
Flow Modulation |  | Flow rate at different modulation levels of flow regulator | 2024-11-04 | 2024-11-04 | 2024-11-06
Filtration |  | Weight of beads filtered by industry-standard that was not filtered by our device | 2024-11-04 | 2024-11-06 | 2024-11-08
Community Comfort | Compatible with Community | User survey feedback | 2024-11-08 | 2024-11-11 | 2024-11-11
Local Sourcing |  | Local availability according to partners at Malawi Polytechnic | 2024-11-05 | 2024-11-08 | 2024-11-08
Cost Efficient |  | Cost of materials according to BOM | 2024-11-05 | 2024-11-08 | 2024-11-08

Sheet: Leakage
Trial | Amount of Unwanted Leakage (ml)
1 | 0
2 | 0
3 | < 1 ml
4 | 0
5 | 0

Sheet: Flow Modulation
 | Water Collected in Beaker
Flow Modulation % | Trial 1 | Trial 2 | Trial 3
100 | 473.2 | 443.6 | 467.3
75 | 360 | 390 | 500
50 | 490 | 470 | 500
25 | 225 | 400 | 400
0 | 0 | 0 | 0

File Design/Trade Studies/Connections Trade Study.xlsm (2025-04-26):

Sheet: Start Here
Trade Study Template for MS Excel
Version 2.0
Copyright © 2014 by Jeffrey Ellis. All rights reserved.
http://jeffreyellis.org
*** START HERE *** The Trade Study Template for MS Excel is a spreadsheet that implements a simple weighted sum method for multiple criteria decision making. It is a .xlsm file that should work with Excel 2007 and later. Instructions: 1. Read the license agreement on the License worksheet. Your continued use of this template constitutes agreement with this license. 2. In the Raw Data worksheet, enter your alternatives under consideration and your evaluation criteria, and enter the raw scores for evaluation criteria for each alternative. 3. In the Utility Functions worksheet, enter the data required to define the utility functions that transform raw scores into utility (on a scale of 0.0 to 1.0) for each evaluation criteria. 4. In the Evaluation worksheet, set and adjust the weighting factors for your evaluation criteria. This worksheet also displays a stacked bar chart of the results, with the alternatives sorted in ranked order. 5. In the Sensitivity Analysis worksheet, you can perform sensitivity analysis on any selected criteria. Detailed instructions on each worksheet appear in a yellow box like this one. Any worksheet that begins with "Calc" is for internal/intermediate calculations. Do not edit these. Do NOT delete any rows or columns, e.g., for unused alternatives or evaluation criteria. Leave them blank instead. The embedded VBA macros will not work properly if you delete any rows.

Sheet: Raw Data
 |  | Pulling |  |  |  |  | Repeated uses
Alternative | Sterility | Strength | Ease of Assembly | Cost | Leakage | Resource Availability | Durability | Biocompatability
Master Bond Epoxy | 9 | 10 | 3 | 6 | 10 | 6 | 10 | 10
Press to Fit | 4 | 6 | 10 | 10 | 2 | 10 | 4 | 10
Tape | 7 | 1 | 1 | 8 | 1 | 10 | 1 | 2
Metal Tubing Clamps | 8 | 8 | 7 | 6 | 8 | 6 | 10 | 10
Min value: | 4 | 1 | 1 | 6 | 1 | 6 | 1 | 2
Max value: | 9 | 10 | 10 | 10 | 10 | 10 | 10 | 10
 |  |  | *** RAW DATA WORKSHEET *** Instructions: 1. Enter your alternatives in column A, replacing the "Alternative 1", "Alternative 2", etc. Delete any unused alternative names; do NOT delete the rows. 2. Enter your evaluation criteria in row 2, replacing the "Criteria 1", "Criteria 2", etc. Delete any unused criteria names; do NOT delete the columns. 2. Enter your evaluation criteria scores for each alternative.

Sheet: Evaluation
 | 0 |  |  |  |  |  |  |  |  |  |  |  |  |  |  |  |  |  |  |  |  |  |  | 25 |  |  |  |  |  |  |  |  |  |  |  |  |  |  |  |  |  |  |  |  |  |  |  |  | 50
Alternative | 1 | 2 | 3 | 4 | 5 | 6 | 7 | 8 | 9 | 10 | 11 | 12 | 13 | 14 | 15 | 16 | 17 | 18 | 19 | 20 | 21 | 22 | 23 | 24 | 25 | 26 | 27 | 28 | 29 | 30 | 31 | 32 | 33 | 34 | 35 | 36 | 37 | 38 | 39 | 40 | 41 | 42 | 43 | 44 | 45 | 46 | 47 | 48 | 49 | 50 | 51 | 52 | 53 | 54 | 55 | 56 | 57 | 58
Master Bond Epoxy
Metal Tubing Clamps
Press to Fit
Tape
#REF!
#REF!
#REF!
#REF!
#REF!
#REF!
#REF!
#REF!
#REF!

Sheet: Calc - Scored
 | Raw data, converted to scores of 0.0 - 1.0 without weighting
Alternative | Sterility | Strength | Ease of Assembly | Cost | Leakage | Resource Availability | Durability | Biocompatability | TOTAL
Master Bond Epoxy | 1.000000 | 1.000000 | 0.222222 | 0.000000 | 1.000000 | 0.000000 | 1.000000 | 1.000000 | 5.222222
Press to Fit | 0.000000 | 0.555556 | 1.000000 | 1.000000 | 0.111111 | 1.000000 | 0.333333 | 1.000000 | 5.000000
Tape | 0.600000 | 0.000000 | 0.000000 | 0.500000 | 0.000000 | 1.000000 | 0.000000 | 0.000000 | 2.100000
Metal Tubing Clamps | 0.800000 | 0.777778 | 0.666667 | 0.000000 | 0.777778 | 0.000000 | 1.000000 | 1.000000 | 5.022222
 |  |  |  | *** CALC - SCORED WORKSHEET *** Do not edit anything in this worksheet. Scores are filled in automatically. These are unweighted utility values on a scale of 0.0 to 1.0 for each evaluation criteria. They are calculated by applying utility functions in the Utility Functions worksheet to the scores in the Raw Data worksheet.

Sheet: Calc - Weighted
 |  | WEIGHTED Scores
RANK | Alternative | Sterility | Strength | Ease of Assembly | Cost | Leakage | Resource Availability | Durability | Biocompatability | TOTAL
1 | Master Bond Epoxy | 10.000000 | 20.000000 | 1.111111 | 0.000000 | 20.000000 | 0.000000 | 20.000000 | 15.000000 | 86.111111
3 | Press to Fit | 0.000000 | 11.111111 | 5.000000 | 5.000000 | 2.222222 | 5.000000 | 6.666667 | 15.000000 | 50.000000
4 | Tape | 6.000000 | 0.000000 | 0.000000 | 2.500000 | 0.000000 | 5.000000 | 0.000000 | 0.000000 | 13.500000
2 | Metal Tubing Clamps | 8.000000 | 15.555556 | 3.333333 | 0.000000 | 15.555556 | 0.000000 | 20.000000 | 15.000000 | 77.444444
 | Weights: | 10.000 | 20.000 | 5.000 | 5.000 | 20.000 | 5.000 | 20.000 | 15.000
 |  |  |  |  |  |  | *** CALC - WEIGHTED WORKSHEET *** Do not edit anything in this worksheet. Weighted scores and ranks are filled in automatically. Weights are set in the Evaluation worksheet, NOT in this worksheet.

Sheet: Calc - Ranked
RANK | Alternative | Sterility | Strength | Ease of Assembly | Cost | Leakage | Resource Availability | Durability | Biocompatability | TOTAL
1 | Master Bond Epoxy | 10.000 | 20.000 | 1.111 | 0.000 | 20.000 | 0.000 | 20.000 | 15.000 | 86.111
2 | Metal Tubing Clamps | 8.000 | 15.556 | 3.333 | 0.000 | 15.556 | 0.000 | 20.000 | 15.000 | 77.444
3 | Press to Fit | 0.000 | 11.111 | 5.000 | 5.000 | 2.222 | 5.000 | 6.667 | 15.000 | 50.000
4 | Tape | 6.000 | 0.000 | 0.000 | 2.500 | 0.000 | 5.000 | 0.000 | 0.000 | 13.500
 |  |  |  |  |  | *** CALC - RANKED WORKSHEET *** Do not edit anything in this worksheet. This sheet automatically sorts the Alternatives and their data (from the Calc - Weighted worksheet) by total score. (Rank = 1 is the highest total score, Rank = 25 is the lowest total score.)

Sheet: Sensitivity Analysis
 | Choose criteria for sensitivity analysis:
 |  | 1
 |  |  |  |  | In Evaluation worksheet, this weight is currently set to:
 | Minimum weight for sensitivity analysis:
 | 0.00 |  |  |  | 10.00
 | Maximum weight for sensitivity analysis:
 | 100.00
 | Across this weight range, highlighted alternatives changed rank as follows: |  | From rank | To rank
 | Master Bond Epoxy |  | #REF! | #REF!
 | #REF! |  | #REF! | #REF!
 | Press to Fit |  | #REF! | #REF!
 | Tape |  | #REF! | #REF!
 | Metal Tubing Clamps |  | #REF! | #REF!
 | #REF! |  | #REF! | #REF!
 | #REF! |  | #REF! | #REF!
 | #REF! |  | #REF! | #REF!
 | #REF! |  | #REF! | #REF!
 | #REF! |  | #REF! | #REF!
 | #REF! |  | #REF! | #REF!
 | #REF! |  | #REF! | #REF!
 | #REF! |  | #REF! | #REF!
 | #REF! |  | #REF! | #REF!
 | #REF! |  | #REF! | #REF!
 | #REF! |  | #REF! | #REF!
 | #REF! |  | #REF! | #REF!
 | #REF! |  | #REF! | #REF!
 | #REF! |  | #REF! | #REF!
 | #REF! |  | #REF! | #REF!
 | #REF! |  | #REF! | #REF!
 | #REF! |  | #REF! | #REF!
 | #REF! |  | #REF! | #REF!
 | #REF! |  | #REF! | #REF!
*** SENSITIVITY ANALYSIS WORKSHEET *** Sensitivity analysis is the process of determining how sensitive the ranking of alternatives is to changes in weighting factors. This worksheet plots the total scores of alternatives against a selected range of values for a chosen weight, to show how the rankings change across these weighting factor values. Instructions: 1. Use the drop-down menu at the top-right to select the evaluation criteria to use for sensitivity analysis. 2. Select the minimum and maximum values for this evaluation criteria's weighting factor. 3. The plot will update accordingly to use these as minimum and maximum values for the weight (x-axis). The table at the right will highlight the alternatives whose rankings change across the chosen range of weighting factor values for the chosen criteria. 4. If you care to, you can see the specific weight values at which an alternative changes its rank in the Calc - SA2 worksheet. | #REF! |  | #REF! | #REF!

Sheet: Utility Functions
*** UTILITY FUNCTIONS WORKSHEET *** A utility function maps the raw scores for an evaluation criteria into a measure of utility, on a scale of 0.0 to 1.0. You should customize the utility functions as needed so the resultant values reasonably represent the utility to you of the raw scores they represent. By default, each utility function is set to linearly map raw data scores from a utility of 0.0 for the minimum raw score, to 1.0 for the maximum raw score. The utility function tables in this worksheet will be interpolated to determine the utility value of each score in the Raw Data worksheet; these utility values appear in the Calc - Scored worksheet. Instructions: You should only edit information in the green boxes. For each evalation criteria,... 1. Choose the appropriate utility function from the drop-down menu. If you want to define your own utility functions, select Custom 1 or Custom 2 from the menu and use the Custom1 or Custom2 columns to provide the utility scores for these functions. Enter utility values on each row, corresponding to the range of raw scores shown in column H (which are in increments of 1/10 the total range, from Min Score to Max Score inclusive). 2. Min Score and Max Score define what raw data range the utitily function maps to. By default these are set to the min and max scores found in the raw data, but you can make the range larger if you wish. (Do NOT change the range so that it excludes any of the raw data scores, or the utility interpolatio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
 |  | Function: | 1 |  |  | Utility Function Calculations -- DO NOT EDIT |  |  |  |  |  |  |  |  |  | User-Defined Utility Functions |  | For Categorical Evaluation Criteria
 |  | Min Score: | 4.00 | Min Util: | 0.00 | Linear |  | Concave |  | Convex |  | S-Curve |  | Concave/Convex
 |  | Max Score: | 9.00 | Max Util: | 1.00 | Inc | Dec | Inc | Dec | Inc | Dec | Inc | Dec | Inc | Dec | Custom1 | Custom2 | Category | Utility
 |  |  |  | Power: | 4.00 | 0.000 | 1.000 | 0.000 | 1.000 | 0.000 | 1.000 | 0.000 | 1.000 | 0.000 | 1.000
 |  | Raw Score | Utility |  |  | 0.100 | 0.900 | 0.344 | 1.000 | 0.0001 | 0.656 | 0.168 | 0.832 | 0.099 | 0.901
 |  | 4.00 | 0.000 |  |  | 0.200 | 0.800 | 0.590 | 0.998 | 0.002 | 0.410 | 0.231 | 0.769 | 0.190 | 0.810
 |  | 4.50 | 0.100 |  |  | 0.300 | 0.700 | 0.760 | 0.992 | 0.008 | 0.240 | 0.310 | 0.690 | 0.269 | 0.731
 |  | 5.00 | 0.200 |  |  | 0.400 | 0.600 | 0.870 | 0.974 | 0.026 | 0.130 | 0.401 | 0.599 | 0.332 | 0.668
 |  | 5.50 | 0.300 |  |  | 0.500 | 0.500 | 0.938 | 0.938 | 0.062 | 0.062 | 0.500 | 0.500 | 0.381 | 0.381
 |  | 6.00 | 0.400 |  |  | 0.600 | 0.400 | 0.974 | 0.870 | 0.130 | 0.026 | 0.599 | 0.401 | 0.668 | 0.332
 |  | 6.50 | 0.500 |  |  | 0.700 | 0.300 | 0.992 | 0.760 | 0.240 | 0.008 | 0.690 | 0.310 | 0.731 | 0.269
 |  | 7.00 | 0.600 |  |  | 0.800 | 0.200 | 0.998 | 0.590 | 0.410 | 0.002 | 0.769 | 0.231 | 0.810 | 0.190
 |  | 7.50 | 0.700 |  |  | 0.900 | 0.100 | 1.000 | 0.344 | 0.656 | 0.0001 | 0.832 | 0.168 | 0.901 | 0.099
 |  | 8.00 | 0.800 |  |  | 1.000 | 0.000 | 1.000 | 0.000 | 1.000 | 0.000 | 1.000 | 0.000 | 1.000 | 0.000
 |  | 8.50 | 0.900
 |  | 9.00 | 1.000
 |  | Function: | 1 |  |  | Utility Function Calculations -- DO NOT EDIT |  |  |  |  |  |  |  |  |  | User-Defined Utility Functions |  | For Categorical Evaluation Criteria
 |  | Min Score: | 1.00 | Min Util: | 0.00 | Linear |  | Concave |  | Convex |  | S-Curve |  | Concave/Convex
 |  | Max Score: | 10.00 | Max Util: | 1.00 | Inc | Dec | Inc | Dec | Inc | Dec | Inc | Dec | Inc | Dec | Custom1 | Custom2 | Category | Utility
 |  |  |  | Power: | 2.00 | 0.000 | 1.000 | 0.000 | 1.000 | 0.000 | 1.000 | 0.000 | 1.000 | 0.000 | 1.000
 |  | Raw Score | Utility |  |  | 0.100 | 0.900 | 0.190 | 0.990 | 0.010 | 0.810 | 0.310 | 0.690 | 0.050 | 0.950
 |  | 1.00 | 0.000 |  |  | 0.200 | 0.800 | 0.360 | 0.960 | 0.040 | 0.640 | 0.354 | 0.646 | 0.099 | 0.901
 |  | 1.90 | 0.100 |  |  | 0.300 | 0.700 | 0.510 | 0.910 | 0.090 | 0.490 | 0.401 | 0.599 | 0.146 | 0.854
 |  | 2.80 | 0.200 |  |  | 0.400 | 0.600 | 0.640 | 0.840 | 0.160 | 0.360 | 0.450 | 0.550 | 0.190 | 0.810
 |  | 3.70 | 0.300 |  |  | 0.500 | 0.500 | 0.750 | 0.750 | 0.250 | 0.250 | 0.500 | 0.500 | 0.231 | 0.231
 |  | 4.60 | 0.400 |  |  | 0.600 | 0.400 | 0.840 | 0.640 | 0.360 | 0.160 | 0.550 | 0.450 | 0.810 | 0.190
 |  | 5.50 | 0.500 |  |  | 0.700 | 0.300 | 0.910 | 0.510 | 0.490 | 0.090 | 0.599 | 0.401 | 0.854 | 0.146
 |  | 6.40 | 0.600 |  |  | 0.800 | 0.200 | 0.960 | 0.360 | 0.640 | 0.040 | 0.646 | 0.354 | 0.901 | 0.099
 |  | 7.30 | 0.700 |  |  | 0.900 | 0.100 | 0.990 | 0.190 | 0.810 | 0.010 | 0.690 | 0.310 | 0.950 | 0.050
 |  | 8.20 | 0.800 |  |  | 1.000 | 0.000 | 1.000 | 0.000 | 1.000 | 0.000 | 1.000 | 0.000 | 1.000 | 0.000
 |  | 9.10 | 0.900
 |  | 10.00 | 1.000
 |  | Function: | 1 |  |  | Utility Function Calculations -- DO NOT EDIT |  |  |  |  |  |  |  |  |  | User-Defined Utility Functions |  | For Categorical Evaluation Criteria
 |  | Min Score: | 1.00 | Min Util: | 0.00 | Linear |  | Concave |  | Convex |  | S-Curve |  | Concave/Convex
 |  | Max Score: | 10.00 | Max Util: | 1.00 | Inc | Dec | Inc | Dec | Inc | Dec | Inc | Dec | Inc | Dec | Custom1 | Custom2 | Category | Utility
 |  |  |  | Power: | 2.00 | 0.000 | 1.000 | 0.000 | 1.000 | 0.000 | 1.000 | 0.000 | 1.000 | 0.000 | 1.000
 |  | Raw Score | Utility |  |  | 0.100 | 0.900 | 0.190 | 0.990 | 0.010 | 0.810 | 0.310 | 0.690 | 0.050 | 0.950
 |  | 1.00 | 0.000 |  |  | 0.200 | 0.800 | 0.360 | 0.960 | 0.040 | 0.640 | 0.354 | 0.646 | 0.099 | 0.901
 |  | 1.90 | 0.100 |  |  | 0.300 | 0.700 | 0.510 | 0.910 | 0.090 | 0.490 | 0.401 | 0.599 | 0.146 | 0.854
 |  | 2.80 | 0.200 |  |  | 0.400 | 0.600 | 0.640 | 0.840 | 0.160 | 0.360 | 0.450 | 0.550 | 0.190 | 0.810
 |  | 3.70 | 0.300 |  |  | 0.500 | 0.500 | 0.750 | 0.750 | 0.250 | 0.250 | 0.500 | 0.500 | 0.231 | 0.231
 |  | 4.60 | 0.400 |  |  | 0.600 | 0.400 | 0.840 | 0.640 | 0.360 | 0.160 | 0.550 | 0.450 | 0.810 | 0.190
 |  | 5.50 | 0.500 |  |  | 0.700 | 0.300 | 0.910 | 0.510 | 0.490 | 0.090 | 0.599 | 0.401 | 0.854 | 0.146
 |  | 6.40 | 0.600 |  |  | 0.800 | 0.200 | 0.960 | 0.360 | 0.640 | 0.040 | 0.646 | 0.354 | 0.901 | 0.099
 |  | 7.30 | 0.700 |  |  | 0.900 | 0.100 | 0.990 | 0.190 | 0.810 | 0.010 | 0.690 | 0.310 | 0.950 | 0.050
 |  | 8.20 | 0.800 |  |  | 1.000 | 0.000 | 1.000 | 0.000 | 1.000 | 0.000 | 1.000 | 0.000 | 1.000 | 0.000
 |  | 9.10 | 0.900
 |  | 10.00 | 1.000
 |  | Function: | 1 |  |  | Utility Function Calculations -- DO NOT EDIT |  |  |  |  |  |  |  |  |  | User-Defined Utility Functions |  | For Categorical Evaluation Criteria
 |  | Min Score: | 6.00 | Min Util: | 0.00 | Linear |  | Concave |  | Convex |  | S-Curve |  | Concave/Convex
 |  | Max Score: | 10.00 | Max Util: | 1.00 | Inc | Dec | Inc | Dec | Inc | Dec | Inc | Dec | Inc | Dec | Custom1 | Custom2 | Category | Utility
 |  |  |  | Power: | 2.00 | 0.000 | 1.000 | 0.000 | 1.000 | 0.000 | 1.000 | 0.000 | 1.000 | 0.000 | 1.000
 |  | Raw Score | Utility |  |  | 0.100 | 0.900 | 0.190 | 0.990 | 0.010 | 0.810 | 0.310 | 0.690 | 0.050 | 0.950
 |  | 6.00 | 0.000 |  |  | 0.200 | 0.800 | 0.360 | 0.960 | 0.040 | 0.640 | 0.354 | 0.646 | 0.099 | 0.901
 |  | 6.40 | 0.100 |  |  | 0.300 | 0.700 | 0.510 | 0.910 | 0.090 | 0.490 | 0.401 | 0.599 | 0.146 | 0.854
 |  | 6.80 | 0.200 |  |  | 0.400 | 0.600 | 0.640 | 0.840 | 0.160 | 0.360 | 0.450 | 0.550 | 0.190 | 0.810
 |  | 7.20 | 0.300 |  |  | 0.500 | 0.500 | 0.750 | 0.750 | 0.250 | 0.250 | 0.500 | 0.500 | 0.231 | 0.231
 |  | 7.60 | 0.400 |  |  | 0.600 | 0.400 | 0.840 | 0.640 | 0.360 | 0.160 | 0.550 | 0.450 | 0.810 | 0.190
 |  | 8.00 | 0.500 |  |  | 0.700 | 0.300 | 0.910 | 0.510 | 0.490 | 0.090 | 0.599 | 0.401 | 0.854 | 0.146
 |  | 8.40 | 0.600 |  |  | 0.800 | 0.200 | 0.960 | 0.360 | 0.640 | 0.040 | 0.646 | 0.354 | 0.901 | 0.099
 |  | 8.80 | 0.700 |  |  | 0.900 | 0.100 | 0.990 | 0.190 | 0.810 | 0.010 | 0.690 | 0.310 | 0.950 | 0.050
 |  | 9.20 | 0.800 |  |  | 1.000 | 0.000 | 1.000 | 0.000 | 1.000 | 0.000 | 1.000 | 0.000 | 1.000 | 0.000
 |  | 9.60 | 0.900
 |  | 10.00 | 1.000
 |  | Function: | 1 |  |  | Utility Function Calculations -- DO NOT EDIT |  |  |  |  |  |  |  |  |  | User-Defined Utility Functions |  | For Categorical Evaluation Criteria
 |  | Min Score: | 1.00 | Min Util: | 0.00 | Linear |  | Concave |  | Convex |  | S-Curve |  | Concave/Convex
 |  | Max Score: | 10.00 | Max Util: | 1.00 | Inc | Dec | Inc | Dec | Inc | Dec | Inc | Dec | Inc | Dec | Custom1 | Custom2 | Category | Utility
 |  |  |  | Power: | 2.00 | 0.000 | 1.000 | 0.000 | 1.000 | 0.000 | 1.000 | 0.000 | 1.000 | 0.000 | 1.000
 |  | Raw Score | Utility |  |  | 0.100 | 0.900 | 0.190 | 0.990 | 0.010 | 0.810 | 0.310 | 0.690 | 0.050 | 0.950
 |  | 1.00 | 0.000 |  |  | 0.200 | 0.800 | 0.360 | 0.960 | 0.040 | 0.640 | 0.354 | 0.646 | 0.099 | 0.901
 |  | 1.90 | 0.100 |  |  | 0.300 | 0.700 | 0.510 | 0.910 | 0.090 | 0.490 | 0.401 | 0.599 | 0.146 | 0.854
 |  | 2.80 | 0.200 |  |  | 0.400 | 0.600 | 0.640 | 0.840 | 0.160 | 0.360 | 0.450 | 0.550 | 0.190 | 0.810
 |  | 3.70 | 0.300 |  |  | 0.500 | 0.500 | 0.750 | 0.750 | 0.250 | 0.250 | 0.500 | 0.500 | 0.231 | 0.231
 |  | 4.60 | 0.400 |  |  | 0.600 | 0.400 | 0.840 | 0.640 | 0.360 | 0.160 | 0.550 | 0.450 | 0.810 | 0.190
 |  | 5.50 | 0.500 |  |  | 0.700 | 0.300 | 0.910 | 0.510 | 0.490 | 0.090 | 0.599 | 0.401 | 0.854 | 0.146
 |  | 6.40 | 0.600 |  |  | 0.800 | 0.200 | 0.960 | 0.360 | 0.640 | 0.040 | 0.646 | 0.354 | 0.901 | 0.099
 |  | 7.30 | 0.700 |  |  | 0.900 | 0.100 | 0.990 | 0.190 | 0.810 | 0.010 | 0.690 | 0.310 | 0.950 | 0.050
 |  | 8.20 | 0.800 |  |  | 1.000 | 0.000 | 1.000 | 0.000 | 1.000 | 0.000 | 1.000 | 0.000 | 1.000 | 0.000
 |  | 9.10 | 0.900
 |  | 10.00 | 1.000
 |  | Function: | 1 |  |  | Utility Function Calculations -- DO NOT EDIT |  |  |  |  |  |  |  |  |  | User-Defined Utility Functions |  | For Categorical Evaluation Criteria
 |  | Min Score: | 6.00 | Min Util: | 0.00 | Linear |  | Concave |  | Convex |  | S-Curve |  | Concave/Convex
 |  | Max Score: | 10.00 | Max Util: | 1.00 | Inc | Dec | Inc | Dec | Inc | Dec | Inc | Dec | Inc | Dec | Custom1 | Custom2 | Category | Utility
 |  |  |  | Power: | 2.00 | 0.000 | 1.000 | 0.000 | 1.000 | 0.000 | 1.000 | 0.000 | 1.000 | 0.000 | 1.000
 |  | Raw Score | Utility |  |  | 0.100 | 0.900 | 0.190 | 0.990 | 0.010 | 0.810 | 0.310 | 0.690 | 0.050 | 0.950
 |  | 6.00 | 0.000 |  |  | 0.200 | 0.800 | 0.360 | 0.960 | 0.040 | 0.640 | 0.354 | 0.646 | 0.099 | 0.901
 |  | 6.40 | 0.100 |  |  | 0.300 | 0.700 | 0.510 | 0.910 | 0.090 | 0.490 | 0.401 | 0.599 | 0.146 | 0.854
 |  | 6.80 | 0.200 |  |  | 0.400 | 0.600 | 0.640 | 0.840 | 0.160 | 0.360 | 0.450 | 0.550 | 0.190 | 0.810
 |  | 7.20 | 0.300 |  |  | 0.500 | 0.500 | 0.750 | 0.750 | 0.250 | 0.250 | 0.500 | 0.500 | 0.231 | 0.231
 |  | 7.60 | 0.400 |  |  | 0.600 | 0.400 | 0.840 | 0.640 | 0.360 | 0.160 | 0.550 | 0.450 | 0.810 | 0.190
 |  | 8.00 | 0.500 |  |  | 0.700 | 0.300 | 0.910 | 0.510 | 0.490 | 0.090 | 0.599 | 0.401 | 0.854 | 0.146
 |  | 8.40 | 0.600 |  |  | 0.800 | 0.200 | 0.960 | 0.360 | 0.640 | 0.040 | 0.646 | 0.354 | 0.901 | 0.099
 |  | 8.80 | 0.700 |  |  | 0.900 | 0.100 | 0.990 | 0.190 | 0.810 | 0.010 | 0.690 | 0.310 | 0.950 | 0.050
 |  | 9.20 | 0.800 |  |  | 1.000 | 0.000 | 1.000 | 0.000 | 1.000 | 0.000 | 1.000 | 0.000 | 1.000 | 0.000
 |  | 9.60 | 0.900
 |  | 10.00 | 1.000
 |  | Function: | 1 |  |  | Utility Function Calculations -- DO NOT EDIT |  |  |  |  |  |  |  |  |  | User-Defined Utility Functions |  | For Categorical Evaluation Criteria
 |  | Min Score: | 1.00 | Min Util: | 0.00 | Linear |  | Concave |  | Convex |  | S-Curve |  | Concave/Convex
 |  | Max Score: | 10.00 | Max Util: | 1.00 | Inc | Dec | Inc | Dec | Inc | Dec | Inc | Dec | Inc | Dec | Custom1 | Custom2 | Category | Utility
 |  |  |  | Power: | 2.00 | 0.000 | 1.000 | 0.000 | 1.000 | 0.000 | 1.000 | 0.000 | 1.000 | 0.000 | 1.000
 |  | Raw Score | Utility |  |  | 0.100 | 0.900 | 0.190 | 0.990 | 0.010 | 0.810 | 0.310 | 0.690 | 0.050 | 0.950
 |  | 1.00 | 0.000 |  |  | 0.200 | 0.800 | 0.360 | 0.960 | 0.040 | 0.640 | 0.354 | 0.646 | 0.099 | 0.901
 |  | 1.90 | 0.100 |  |  | 0.300 | 0.700 | 0.510 | 0.910 | 0.090 | 0.490 | 0.401 | 0.599 | 0.146 | 0.854
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

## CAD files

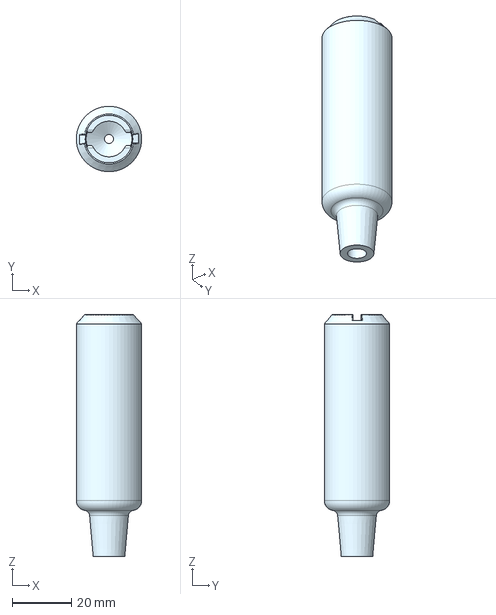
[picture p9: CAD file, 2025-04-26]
STEP Files/V3 Transfusion Set/LOWER ASSEMBLY V3.step
22.0 x 22.0 x 81.4 mm

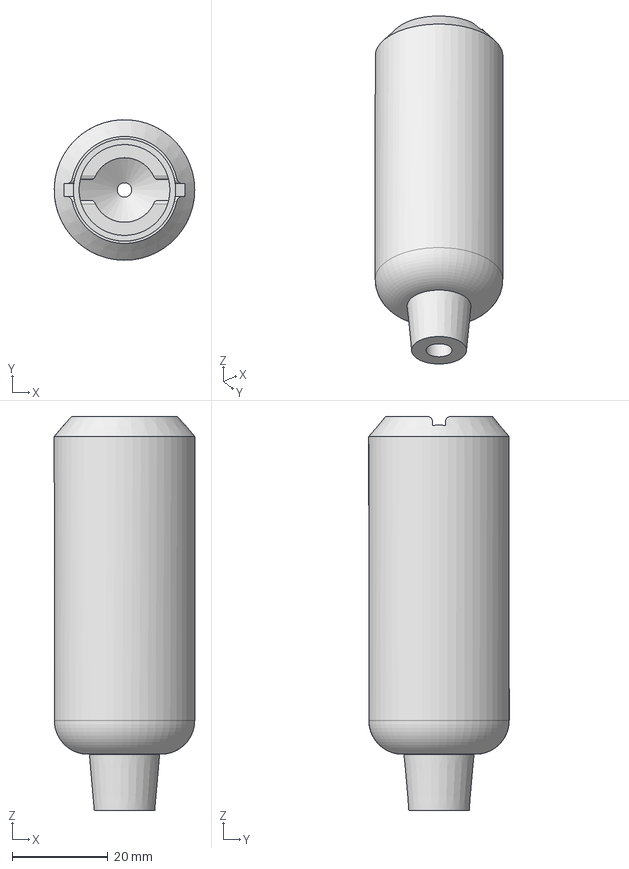
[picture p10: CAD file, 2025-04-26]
STEP Files/V2 Transfusion Set (Working)/LOWER ASSEMBLY [V2].step
29.4 x 29.4 x 82.4 mm

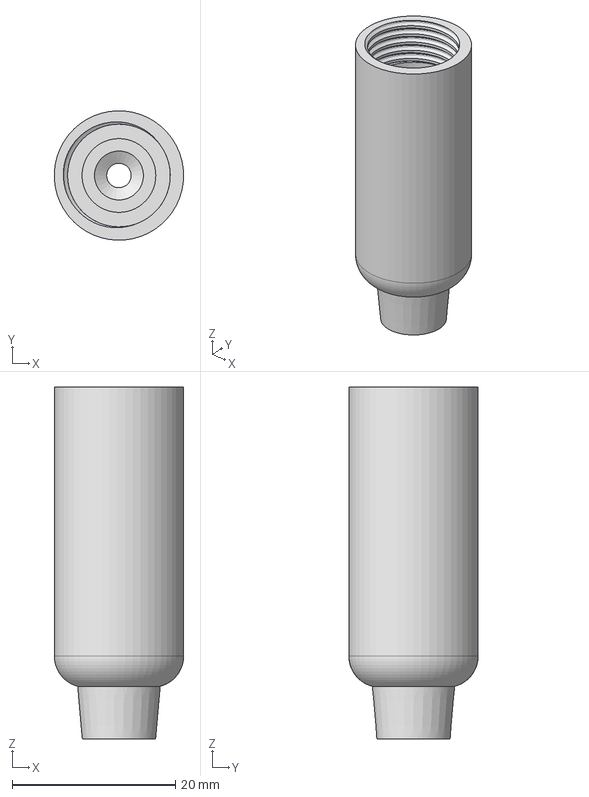
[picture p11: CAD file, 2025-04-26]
STEP Files/V1 Transfusion Set/LOWER ASSEMBLY [V1].step
15.9 x 15.9 x 43.2 mm

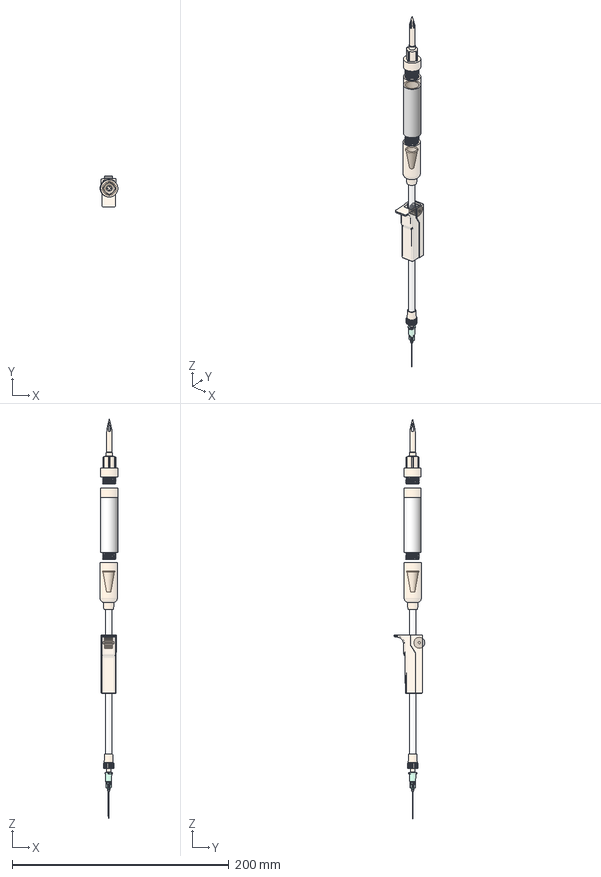
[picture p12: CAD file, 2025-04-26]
STEP Files/V1 Transfusion Set/Transfusion Set [V1].step
16.4 x 28.5 x 369.2 mm
UPPER TUBING
FILTER
LOWER ASSEMBLY
FEMALE CONNECTOR
SPIKE V1
Roller Clamp Wheel V2
Roller Clamp Body V2
Tube
Luer_Lock_Needle
MALE CONNECTOR

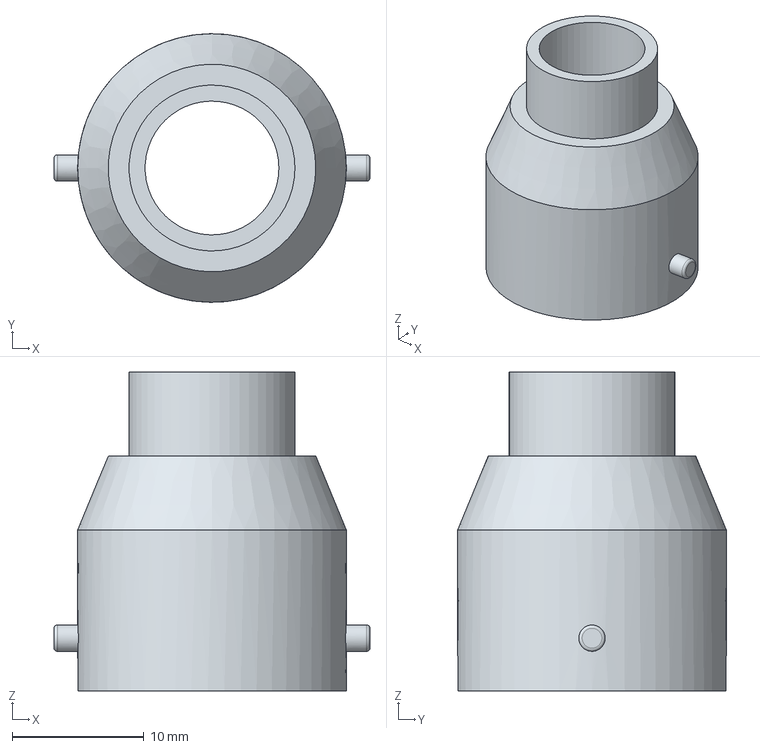
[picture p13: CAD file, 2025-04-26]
STEP Files/V2 Transfusion Set (Working)/MALE CONNECTOR [V2].step
24.0 x 20.4 x 24.2 mm

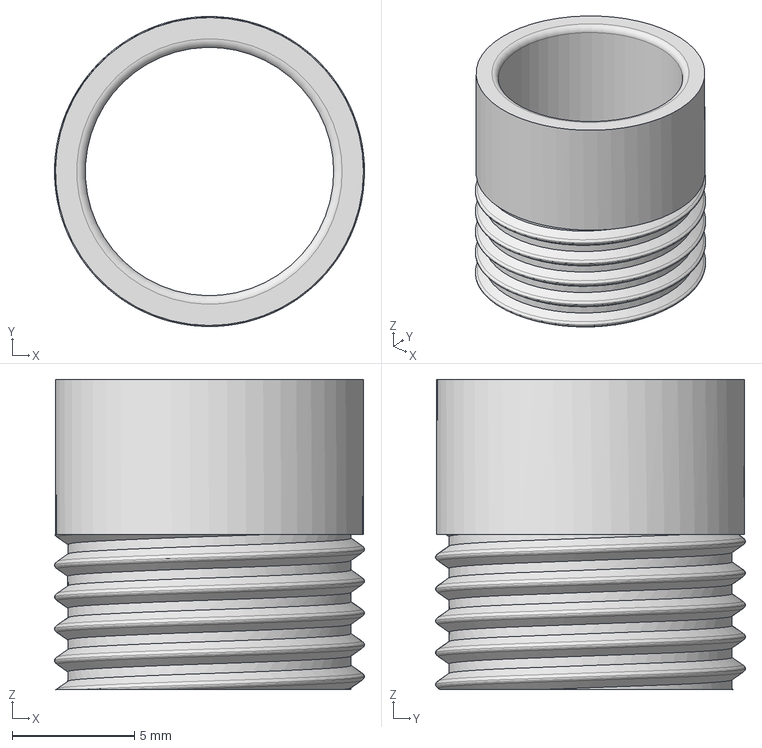
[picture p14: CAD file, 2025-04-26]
STEP Files/V1 Transfusion Set/MALE CONNECTOR [V1].step
12.7 x 12.7 x 12.7 mm

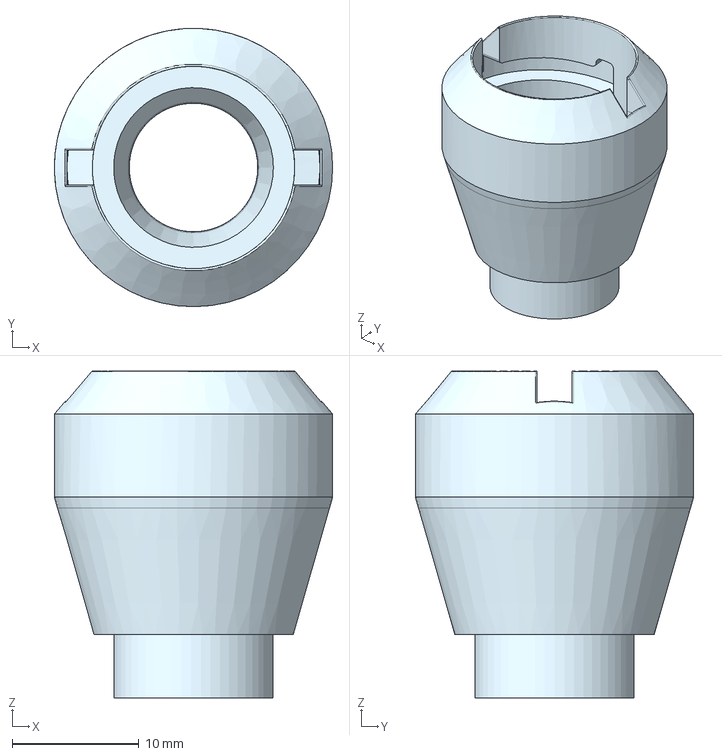
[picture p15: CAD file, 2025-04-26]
STEP Files/V3 Transfusion Set/FEMALE CONNECTOR V3.step
22.0 x 22.0 x 25.8 mm

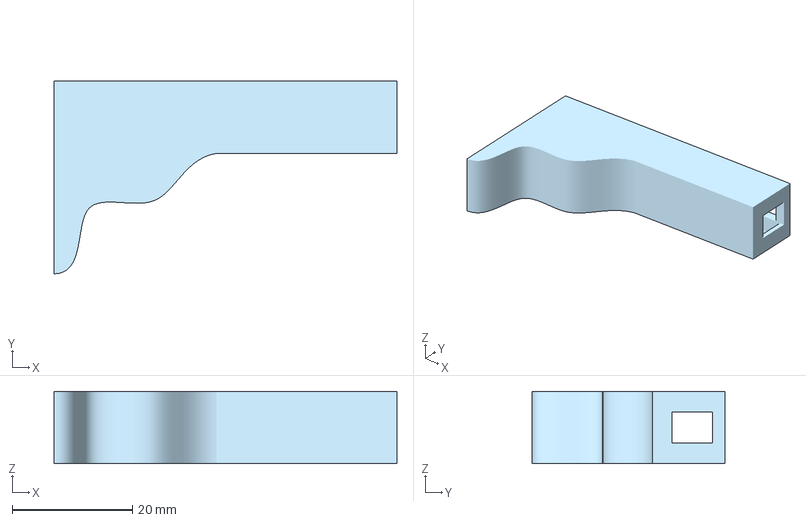
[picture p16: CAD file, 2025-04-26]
STEP Files/V1 Transfusion Set/Roller Clamp Body [V1].step
57.0 x 32.0 x 12.0 mm

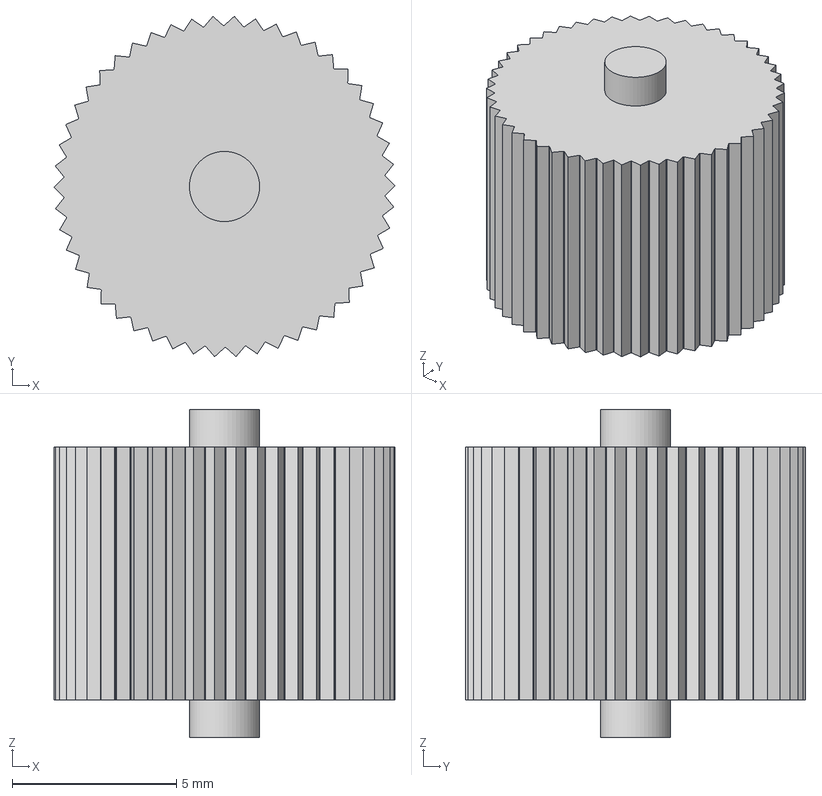
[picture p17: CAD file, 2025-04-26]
STEP Files/V2 Transfusion Set (Working)/Roller Clamp Wheel [V2].step
10.4 x 10.4 x 10.0 mm

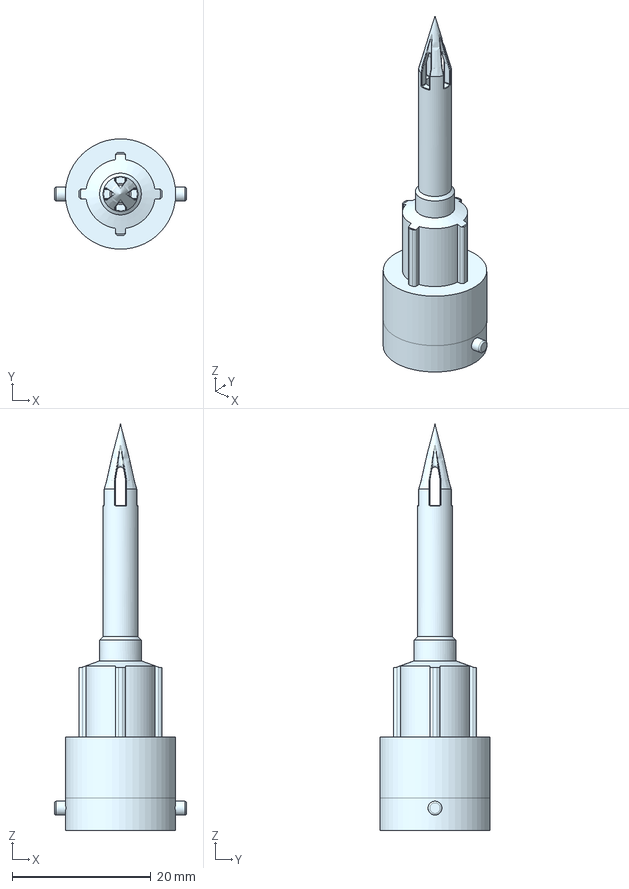
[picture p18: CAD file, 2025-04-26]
STEP Files/V3 Transfusion Set/SPIKE V3.step
19.0 x 15.9 x 58.4 mm

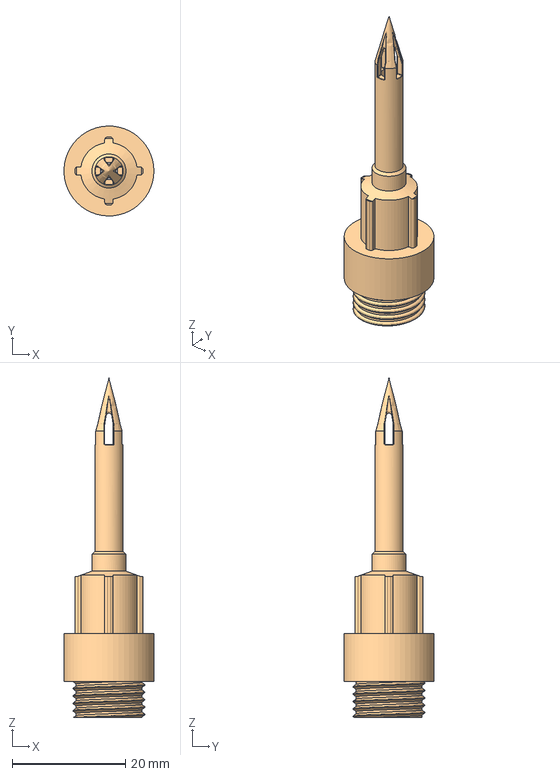
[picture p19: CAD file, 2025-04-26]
STEP Files/V1 Transfusion Set/SPIKE [V1].step
15.9 x 15.9 x 59.9 mm

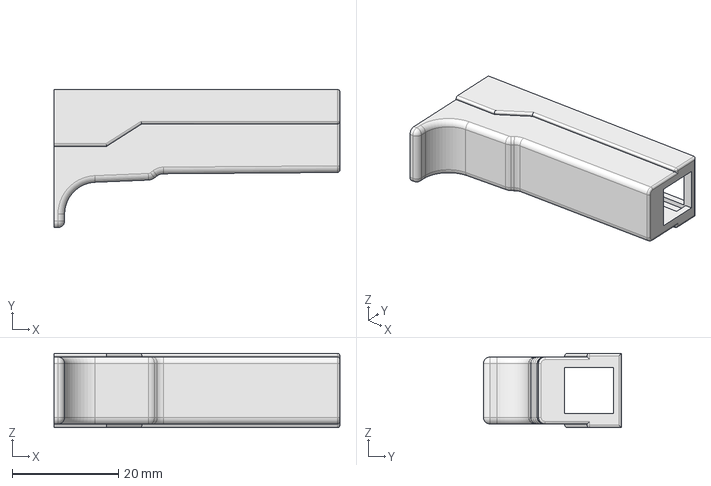
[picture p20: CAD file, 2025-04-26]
STEP Files/V2 Transfusion Set (Working)/Roller Clamp Body [V2].step
53.8 x 26.0 x 14.0 mm

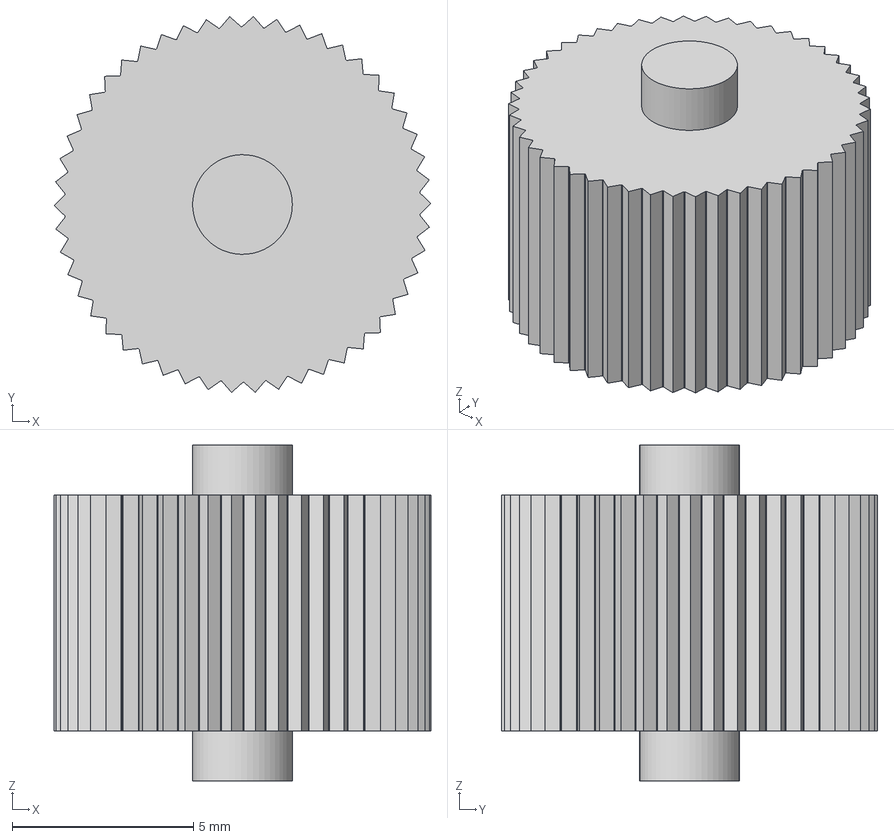
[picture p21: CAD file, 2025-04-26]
STEP Files/V3 Transfusion Set/Roller Clamp Wheel V3.step
10.4 x 10.4 x 9.25 mm

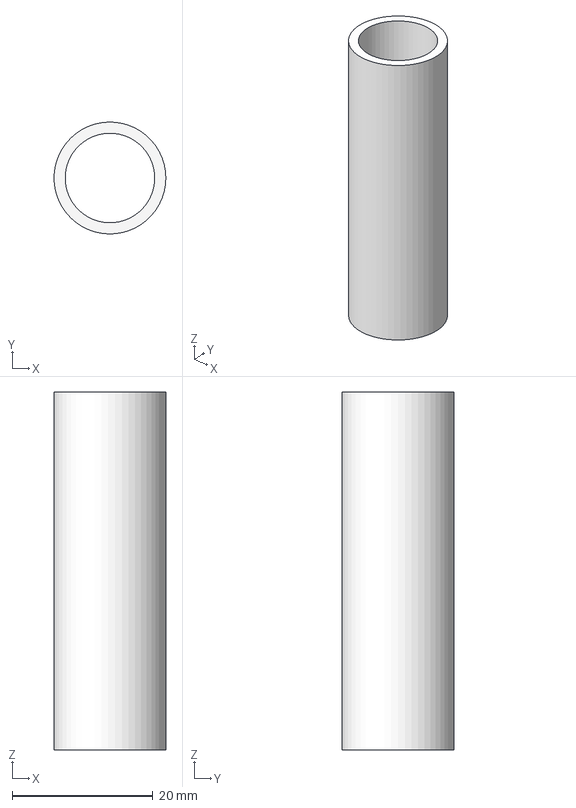
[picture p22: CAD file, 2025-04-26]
STEP Files/V1 Transfusion Set/UPPER TUBING [V1].step
15.9 x 15.9 x 50.8 mm

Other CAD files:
STEP Files/V2 Transfusion Set (Working)/FEMALE CONNECTOR [V2].step
STEP Files/V3 Transfusion Set/O-Ring V3.step
STEP Files/V1 Transfusion Set/FILTER [V1].step
STEP Files/V2 Transfusion Set (Working)/Transfusion Set [V2}.step
STEP Files/V2 Transfusion Set (Working)/FILTER CAGE [V2}.step
STEP Files/V2 Transfusion Set (Working)/O-RING TESTER [V2].step
STEP Files/V2 Transfusion Set (Working)/SPIKE [V2].step
STEP Files/V3 Transfusion Set/LEUR LOCK V3.step
STEP Files/V3 Transfusion Set/MALE CONNECTOR V3.step
STEP Files/V3 Transfusion Set/Roller Clamp Body Lower V3.step
STEP Files/V3 Transfusion Set/Roller Clamp Body Upper V3.step

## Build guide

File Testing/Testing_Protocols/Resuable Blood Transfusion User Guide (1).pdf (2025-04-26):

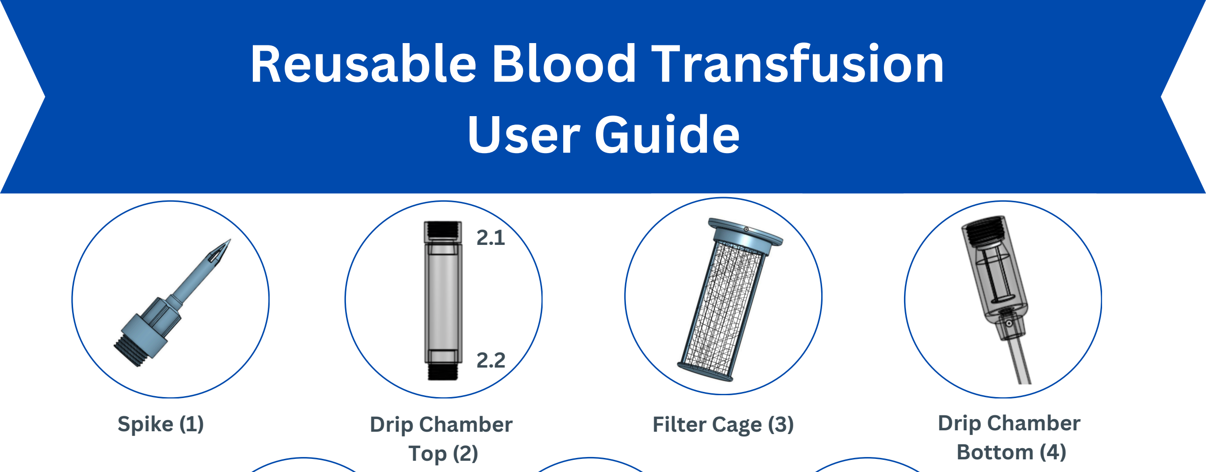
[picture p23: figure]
Drip Chamber Top (2); Drip Chamber Bottom (4); Reusable Blood Transfusion User Guide; Spike (1); Filter Cage (3)
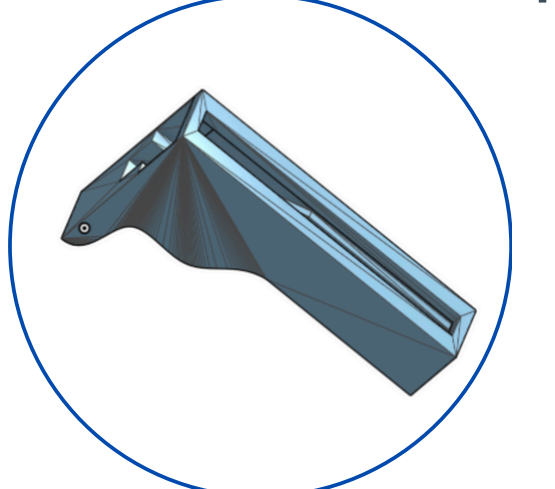
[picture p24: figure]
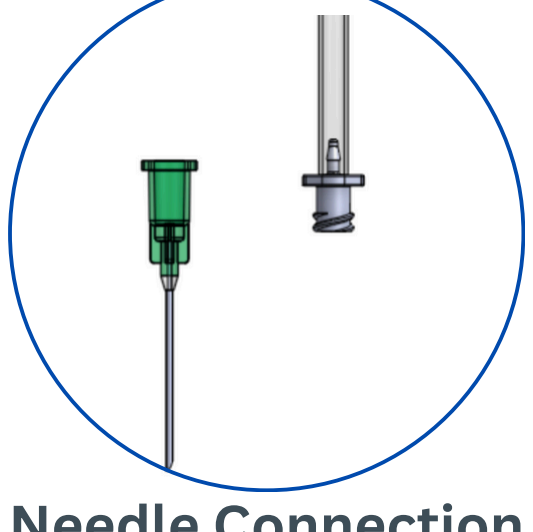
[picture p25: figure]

Assembly | Disassembly/
1.Obtain components listed above | Sterilization

Thread the bottom of the tubing (6) through
the flow regulator (large part of flow
regulator upright) (5)

2.

3.Place filter (3) into drip chamber bottom (4) Screw in the drip chamber top (2.2) to the drip chamber bottom (4)

4.

Screw in the spike (1) to the drip chamber (2.1)

5.

Attach the needle connection (7) to the bottom of the tubing (6)

6.

Deconstruct the transfusion set, throwing away the needle

1.

Place the __ separate components into the wash prior to autoclave

2.

3.Transfer the components into the autoclave 4.Start autoclave cycle
Remove components when the cycle is finished

5.

Flow Regulator (5) | Needle Connection (7)
Tubing (6)

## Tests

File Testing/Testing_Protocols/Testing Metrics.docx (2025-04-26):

# Testing Metrics

~~Blood bag~~

Spike

Connector: Spike-DC (squeeze)

DC (squeeze)

Connector: DC (squeeze) - DC (hard)

DC (hard)

Interface: DC (hard) - Filter

Filter

Connector: DC (hard) - Tubing

Tubing

Connector: Tubing-Luer lock base

Luer lock

Connector: Luer lock-needle

Needle

# Safety

## Bacteria Removal

Ability to remove bacteria from components 1, 2, 5, 10, 25, 50, 100, 150, 200x through autoclave

- Execute for
  - Negative control: surgical tool/ metal component
  - Our components
- Control: Swab component before adding bacteria, plate, incubate for 48 hours, check for colonies
- Testing: Pipette bacteria into components, incubate for 48 hours, check for colonies

## Blood Adhesion

Amount of blood that would get stuck in components 1, 2, 5, 10, 25, 50, 100, 150, 200x through autoclave

- Execute for
  - Negative control: metal tube
  - Our components
- Control: Measure weight of piece before testing and at every other point when measurement is conducted for the component, compare to the ratio of the metal

## Biocompatibility

- Epoxy resin
- Test for potential toxins

# Durability

Measure all at 1, 2, 5, 10, 25, 50, 100, 150, 200x through autoclave

## Tensile Strength

- Cut piece: measure stress/strain curve downstairs
- Cut piece, make sure can endure standard force set by tugging

## Flexibility

- Purpose: Make sure it is still as easy to move around, place in arm, store in spool
- Do a quality test: Have people score it on a scale of 1-10

## Color Change

- Qualitative observation at each cycle, compare to non-autoclaved material
- Passes test if color change does not impair ability to see level of blood

# Air Tightness

## Leakage

Measure without autoclaving, establish baseline

- Run PBS through at least 10x, check if liquid drips out

## Interface Stability

- Glues: torsion test

## Material Viability

Measure all at 1, 2, 5, 10, 25, 50, 100, 150, 200x through autoclave

- Plug into bag, run PBS through tubing after each cycle, make sure no liquid seeps out

# Use Requirements

## Ease of Use

Setup

Survey of doctors and nurses on how they use it

## Flow Regulation

# Community Standards

## Community Comfort

Survey of how comfortable they are with

## Local Sourcing

Contact client,

## Cost Efficacy

Less than $5 per use

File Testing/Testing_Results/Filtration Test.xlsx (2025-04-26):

Trial No | Weight of beads (aim for 100mg) | Filter weight after expirement | Difference | Standard Filter Original Weight (mg)
1 | 100.9 | 1523.9 | 0 | 1523.9
2 | 106 | 1523.8 | -0.1 | 1523.9
3 | 126.8 | 1524 | 0.1
4 | 113.1 | 1524 | 0.1
5 | 119.2 | 1523.8 | -0.1
 |  | Average | 0

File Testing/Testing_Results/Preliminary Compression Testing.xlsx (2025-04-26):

 | Lower assembly lateral | Spike lateral | Female connector lateral | Male connector lateral | Luer lock lateral
Trial 1 (lbs) | >350 | 350 | 157 | 81 | 305
Trial 2 (lbs) | >350 | 262 | 259 | 46
Average (lbs) | 350 | 306 | 208 | 63.5 | 305
Average (N) | 1556.877 | 1361.15532 | 925.22976 | 282.46197 | 1356.7071

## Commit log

2025-04-26 Bring all old documentation to new repository
    [Blood_WA5 TestingLog.xlsx, Connections Trade Study.xlsm, FEMALE CONNECTOR [V2].step, FILTER CAGE [V2}.step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]
2025-04-26 added all of spring 2025 files
    [Bill of Materials.xlsx]
2025-04-26 Add v3 set to CAD files
    [FEMALE CONNECTOR V3.step, LEUR LOCK V3.step, LOWER ASSEMBLY V3.step, MALE CONNECTOR V3.step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]
